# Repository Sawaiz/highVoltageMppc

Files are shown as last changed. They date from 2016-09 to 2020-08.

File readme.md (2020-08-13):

# MPPC High Voltage
Surface mount module that provides 52.5V to 57.5V in 20mV increments. Also contains a 2 input 24bit ADC to allow for closed loop control of the voltage, and read in a thermistor mounted near the sensor.

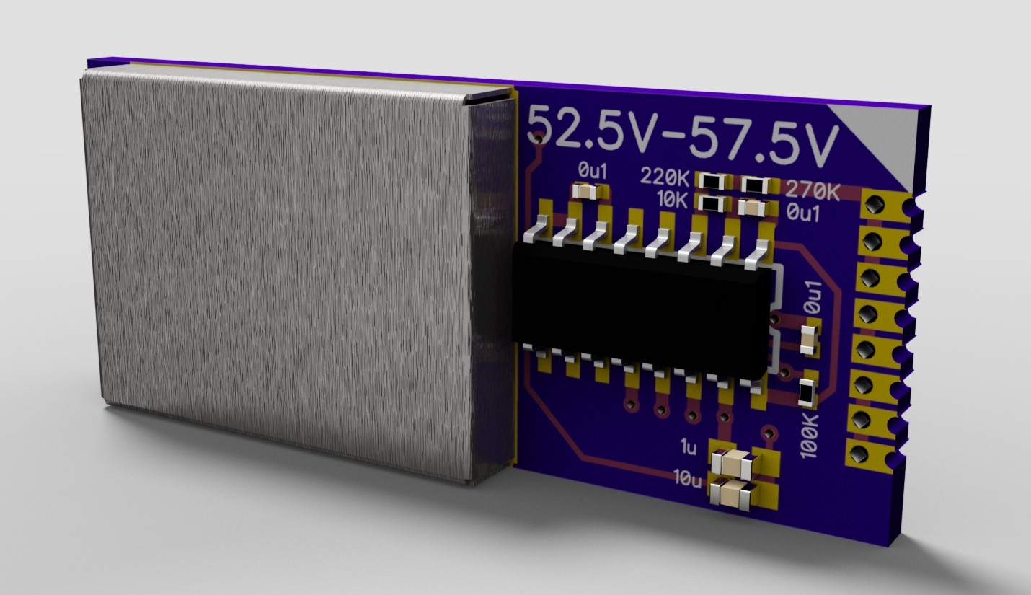
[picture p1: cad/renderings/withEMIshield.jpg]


## Hardware
The module uses a MAX1932 APD bias voltage boost converter and NAU7802SGI 24bit Analog to Digital converter (ADC) for reading temperature and output voltage.

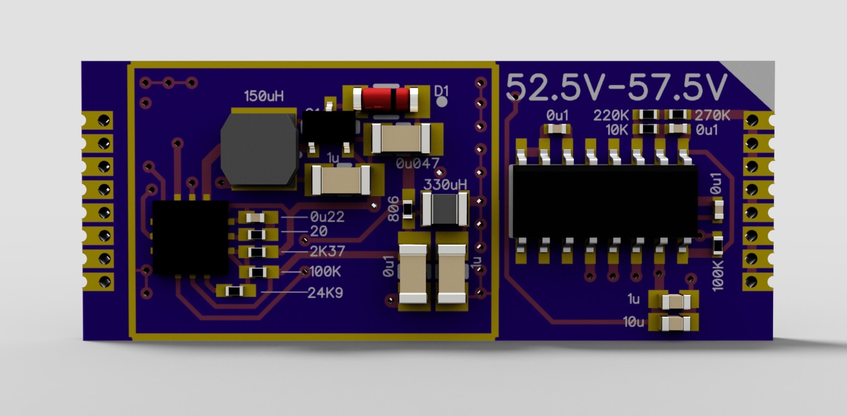
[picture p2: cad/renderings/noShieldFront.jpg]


### High Voltage
The module uses a [MAX1932](http://datasheets.maximintegrated.com/en/ds/MAX1932.pdf) APD bias voltage boost converter to maintain the output voltage. The voltage range, and step size is dictated with setting R2, R3, and R4. The minimum and maximum voltage set using the equations for on page 7 of the datasheet, and there are 8 bits (256) intermediate values that are possible. The high switching portion was designed with general SMPS design requirements (short high current loops, separated ground planes, EMI shielding) providing a low ripple output (<5mVpp ripple) and no significant back EMF.

### ADC
The analog to digital converter is a one designed for high precision and low sampling rate. The [NAU7802SGI](http://www.nuvoton.com/resource-files/NAU7802%20Data%20Sheet%20V1.7.pdf) is marketed at the load sensing market, but the high precision and low sampling rate lends itself well to the closed loop control and monitoring application. The high voltage is divided by 100 and the thermistor is put across a equivalent 100K static resistor to go along with he 100K NTC found on the MPPC sensor module to act as a voltage divider.

## Software
Each module has two buses that run to it. The following lists pins and their functions.

| Pin | Label | Description               |
| --- | ----- | ------------------------- |
|1    | 3V3   | Regulated 3.3V in         |
|2    | CS    | **SPI** bus Chip Select   |
|3    | SCLK  | **SPI** bus clock         |
|4    | DIN   | **SPI** bus data in       |
|5    | GND   | Common Ground             |
|6    | DRDY  | ADC conversion done       |
|7    | SCL   | **I2C** bus clock         |
|8    | SDA   | **I2C** bus data          |

### High Voltage
The SPI bus is connected directly to the MAX1932. Chip select is active low and data is sent MSB (most significant bit first). Sending bytes to it sets the voltage. Setting them to 0x00 turns off the DC-DC converter portion. As values increase to 0xFF (127), the output voltage falls, linearly.

```Arduino
//Example Arduino code that loops through all voltages.
//SCLK --> Pin 13 for Uno or Duemilanove
//DIN ---> Pin 11 for Uno or Duemilanove

#include <SPI.h>
#define CS 2 //Any pin

void setup(){
	Serial.begin(9600);
	pinMode(CS, OUTPUT);
	digitalWrite(CS, HIGH);
	SPI.begin();
	SPI.setBitOrder(MSBFIRST);
}

void loop(){
	for(int i = 0 ; i < 256 ; i++){
		digitalWrite(CS, LOW);
		SPI.transfer(i);
		digitalWrite(CS, HIGH);
		Serial.println(i);
	}
}
```

### ADC
The ADC communicates through the I2C bus, the device address is permanently programed to *0101010* (0x2A). It is fully compliant with the I2C protocol and the datasheet has the register map (page 28) and protocol description (page 14).

```Arduino
//Example Arduino code to read back the two inputs.
#include <Wire.h>
unsigned long adcVal;

void setup(){
	Serial.begin(9600);
	Wire.begin();
}

void loop(){
	// step 1: instruct sensor to read
	Wire.beginTransmission(42); // transmit to device #42 (0x2A)
	Wire.write(byte(0x00));      // control address byte (0x)
	Wire.write(byte(0x00));      // data byte (0x)
	Wire.endTransmission();      // stop transmitting

	// step 2: wait for readings to happen
	delay(1000);

	// step 3: request reading from sensor
	Wire.requestFrom(42, 3);    // request 2 bytes from slave device #42

	// step 4: receive reading from sensor
	if (3 <= Wire.available()) { // if two bytes were received
		adcVal = Wire.read();      // receive byte one (overwrites previous reading)
		adcVal = adcVal << 8;      // shift byte to make room for new byte
		adcVal = Wire.read();      // receive high two
		adcVal = adcVal << 8;      // shift both bytes
		adcVal |= Wire.read();     // receive low byte
		Serial.println(adcVal);    // print the reading
	}
}
```

## Archived
Archived, HV intergrated into MPPC interface from v1.1.

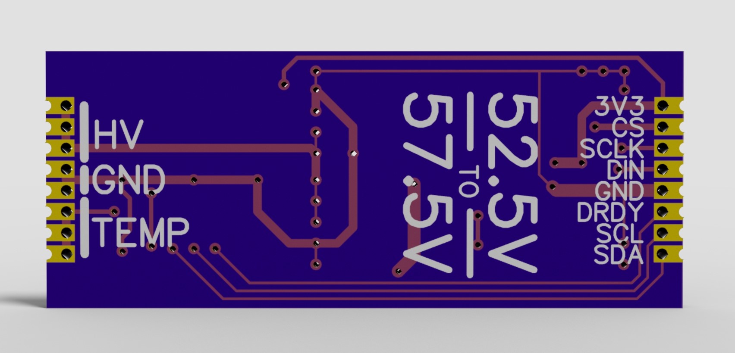
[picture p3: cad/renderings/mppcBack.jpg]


[mppcBack]: cad/renderings/mppcBack.jpg "View of Back of Board"
[noShieldFront]: cad/renderings/noShieldFront.jpg "Direct front view"
[withEMIshield]: cad/renderings/withEMIshield.jpg "Board rendering with EMI shield"

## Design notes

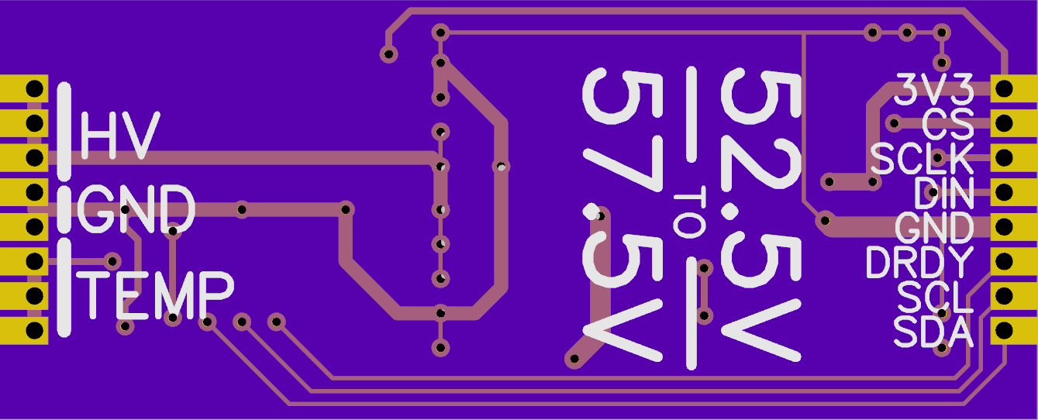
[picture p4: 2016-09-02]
cad/decal/highVoltageMppcBack.png

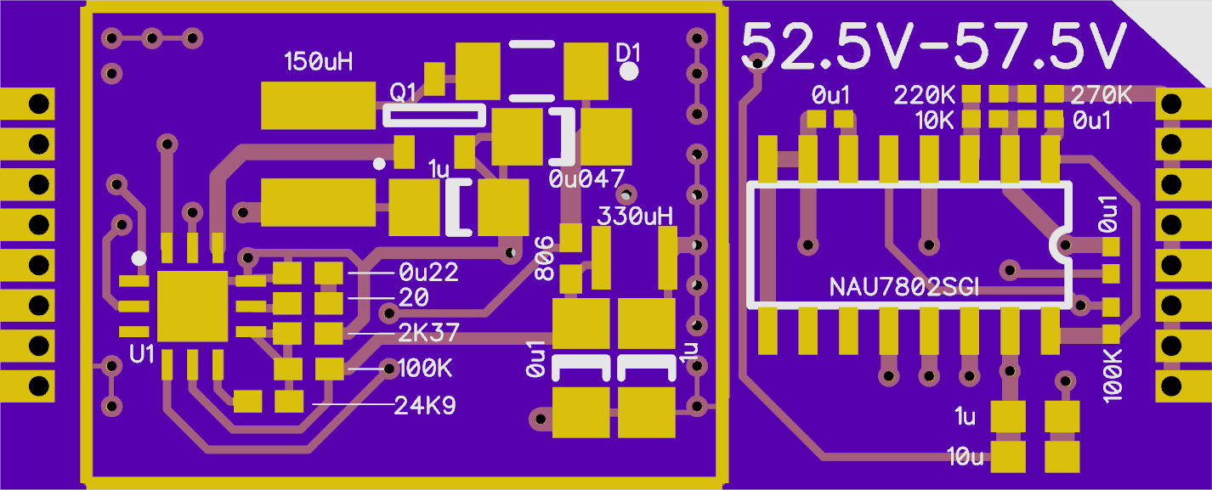
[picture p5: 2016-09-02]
cad/decal/highVoltageMppcFront.png

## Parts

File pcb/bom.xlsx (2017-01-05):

Ref-Des | Function | Description | P/N | Digikey P/N | QTY | Unit Price | Extended Price | URL
C1 | Input Decoupling | 1µF 16V Ceramic Capacitor X7R 1206 | 160R18W105KV4E | 709-1068-1-ND | 1 | $0.0890 | $0.09 | http://www.digikey.com/scripts/DkSearch/dksus.dll?Detail&itemSeq=188836551&uq=635911598142349451
C2 | Boost Capacitor | 0.047µF 500V Ceramic Capacitor X7R 1206 | C1206C473KCRACTU | 399-6743-1-ND | 1 | $0.1300 | $0.13 | http://www.digikey.com/scripts/DkSearch/dksus.dll?Detail&itemSeq=188836455&uq=635911598142339439
C3 | Pre Filter Capacitor | 0.10µF 250V Ceramic Capacitor X7R 1206 | C1206C104KARACTU | 399-4674-1-ND | 1 | $0.1485 | $0.15 | http://www.digikey.com/scripts/DkSearch/dksus.dll?Detail&itemSeq=188836482&uq=635911598142349451
C4 | Post Filter Capacitor | CAP CER 1UF 100V X7R 1206 | 12061C105KAT2A | 478-6226-1-ND | 1 | $0.1570 | $0.16 | http://www.digikey.com/scripts/DkSearch/dksus.dll?Detail&itemSeq=188836361&uq=635911598142339439
C5 | Compensation Capacitor | CAP CER 0.22UF 16V Y5V 0402 | CL05F224ZO5NNNC | 1276-1060-1-ND | 1 | $0.0112 | $0.01 | http://www.digikey.com/scripts/DkSearch/dksus.dll?Detail&itemSeq=188836589&uq=635911598142349451
D1 | Boost Diode | DIODE GEN PURP 100V 200MA SOD80 | LL4148 | LL4148FSCT-ND | 1 | $0.0420 | $0.04 | http://www.digikey.com/scripts/DkSearch/dksus.dll?Detail&itemSeq=188146539&uq=635911598142339439
L1 | Boost Inductor | FIXED IND 150UH 320MA 2.4 OHM | SRN4018-151M | SRN4018-151MCT-ND | 1 | $0.2400 | $0.24 | http://www.digikey.com/scripts/DkSearch/dksus.dll?Detail&itemSeq=188145546&uq=635911598142329427
L2 | Smoothing Inductor | FIXED IND 330UH 90MA 15.99 OHM | CBC2518T331K | 587-3059-1-ND | 1 | $0.1400 | $0.14 | http://www.digikey.com/scripts/DkSearch/dksus.dll?Detail&itemSeq=188145512&uq=635911598142319415
Q1 | Boost Switch | MOSFET N-CH 100V 0.17A SOT-23 | BSS123L | BSS123LCT-ND | 1 | $0.1032 | $0.10 | http://www.digikey.com/scripts/DkSearch/dksus.dll?Detail&itemSeq=188145567&uq=635911598142329427
R1 | Current Sens Resistor | RES SMD 806 OHM 0.1% 1/16W 0402 | RT0402BRD07806RL | YAG1481CT-ND | 1 | $0.1276 | $0.13 | http://www.digikey.com/scripts/DkSearch/dksus.dll?Detail&itemSeq=188837307&uq=635911598142359463
R2, R6 | Adjustment Span/Temp | RES SMD 100K OHM 0.1% 1/16W 0402 | RT0402BRD07100KL | YAG1343CT-ND | 2 | $0.1276 | $0.26 | http://www.digikey.com/scripts/DkSearch/dksus.dll?Detail&itemSeq=188837329&uq=635911598142359463
R3 | Minimum Voltage Res | RES SMD 2.37KOHM 0.1% 1/16W 0402 | CPF0402B2K37E1 | A102770CT-ND | 1 | $0.2082 | $0.21 | http://www.digikey.com/scripts/DkSearch/dksus.dll?Detail&itemSeq=188837419&uq=635911598142369475
R4 | DAC Resistor | RES SMD 24.9KOHM 0.1% 1/16W 0402 | RT0402BRD0724K9L | YAG1393CT-ND | 1 | $0.1276 | $0.13 | http://www.digikey.com/scripts/DkSearch/dksus.dll?Detail&itemSeq=188837348&uq=635911598142359463
R5 | Compensation Res | RES SMD 20 OHM 0.1% 1/16W 0402 | CPF0402B20RE1 | A102706CT-ND | 1 | $0.1973 | $0.20 | http://www.digikey.com/scripts/DkSearch/dksus.dll?Detail&itemSeq=188837408&uq=635911598142369475
U1 | Boost Controller | IC SUPPLY BIAS APD 12-TQFN | MAX1932ETC+T | MAX1932ETC+TCT-ND | 1 | $7.2828 | $7.28 | http://www.digikey.com/scripts/DkSearch/dksus.dll?Detail&itemSeq=188145609&uq=635911598142329427
U2 | ADC | IC ADC 24BIT I2C/SRL 16-SOP | NAU7802SGI | NAU7802SGI-ND | 1 | $1.3442 | $1.34 | http://www.digikey.com/product-search/en/rf-if-and-rfid/rf-shields/3539677?k=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
C6 | .1uF | 0.10µF 10V Ceramic Capacitor X5R 0402 | CL05A104KP5NNNC | 1276-1022-1-ND | 2 | $0.0048 | $0.01 | http://www.digikey.com/product-detail/en/murata-electronics-north-america/GRM155R71C104KA88J/490-6328-2-ND/2610892
C7 | 1uF | 1µF 6.3V Ceramic Capacitor X6S 0402 | GRM155C80J105KE15D | 490-6281-1-ND | 1 | $0.0055 | $0.01 | http://www.digikey.com/product-detail/en/murata-electronics-north-america/GRM155C80J105KE15D/490-6281-2-ND/2610795
C8 | 10uF | 10µF 6.3V Ceramic Capacitor X5R 0603 | GRM155R60G106ME44D | 490-10693-1-ND | 1 | $0.0380 | $0.04 | http://www.digikey.com/product-detail/en/murata-electronics-north-america/GRM155R60G106ME44D/490-10693-2-ND/4905101
S1 | RF Shield | RFI SHIELD CAN 20X15X3MM | S02-20150300 | 952-2632-ND | 1 | $3.5300 | $3.53 | http://www.digikey.com/product-search/en/rf-if-and-rfid/rf-shields/3539677?k=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
R7 | 220k 1% | RES SMD 220K OHM 1% 1/16W 0402 | RC0402FR-07220KL | 311-220KLRCT-ND | 1 | $0.0054 | $0.01 | http://www.digikey.com/scripts/DkSearch/dksus.dll?Detail&itemSeq=203632236&uq=636058256422392383
R9 | 270k 1% | RES SMD 270K OHM 1% 1/16W 0402 | RC0402FR-07270KL | 311-270KLRCT-ND | 1 | $0.0054 | $0.01 | http://www.digikey.com/scripts/DkSearch/dksus.dll?Detail&itemSeq=203632249&uq=636058256422402384
R8 | 10k 0.1% | RES SMD 10K OHM 1% 1/16W 0402 | RC0402FR-0710KL | 311-10.0KLRCT-ND | 1 | $0.0054 | $0.01 | http://www.digikey.com/scripts/DkSearch/dksus.dll?Detail&itemSeq=203632266&uq=636058256422402384

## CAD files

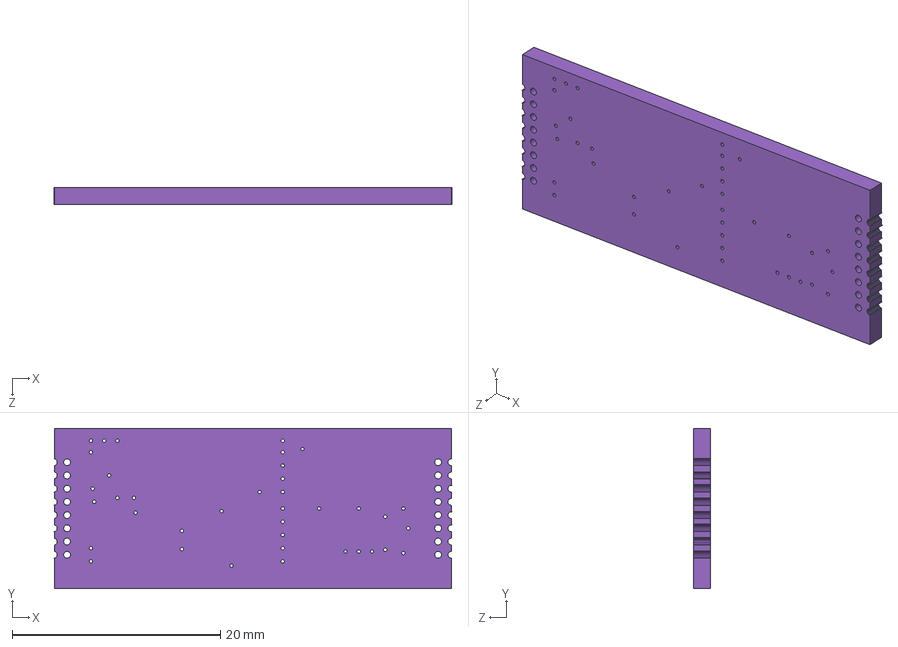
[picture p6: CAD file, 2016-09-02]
cad/highVoltageMppc.step
38.2 x 15.4 x 1.60 mm

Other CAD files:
cad/electronics/2.54 Breakaway/1x1.iam
cad/electronics/2.54 Breakaway/1x6.iam
cad/electronics/2.54 Breakaway/Holder.ipt
cad/electronics/2.54 Breakaway/Pin.ipt
cad/electronics/2.54 Breakaway/PinRight1.ipt
cad/electronics/2.54 Breakaway/PinRight2.ipt
cad/electronics/S02-20150300.ipt
cad/electronics/SOP-16.ipt
cad/electronics/SOT23-3.ipt
cad/electronics/SRN4018.ipt
cad/electronics/capacitor-0402.ipt
cad/electronics/capacitor-0603.ipt
cad/electronics/capacitor-1206.ipt
cad/electronics/capacitor.ipt
cad/electronics/chipResistor.ipt
cad/electronics/chipResistor/chipResistor-0402.ipt
cad/electronics/inductor-1007.ipt
cad/electronics/inductor.ipt
cad/electronics/qfn.ipt
cad/electronics/qfn/qfn-12.ipt
cad/electronics/sod-80.ipt
cad/highVoltageMppcBoard.iam
cad/highVoltageMppcBoard.ipt

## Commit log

2016-03-02 Cad Design Done
    [1x6.iam, 2x4RibbonConnector.ipt, 2x4header.ipt, 788640001.iam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]
2016-03-27 Batch of 24 made
    [1x1.iam, 1x6.iam, highVoltageMppc.iam, pcb.ipt]
2016-04-06 Remaned PCB file to avoid confilts when used as dependecy
    [highVoltageMppcPcb.ipt]
2016-04-06 Reloaded project to fix pcb path
    [1x1.iam, 1x6.iam, highVoltageMppc.iam]
2016-04-06 Renamed Decal FIles to prevent clashes
    [highVoltageMppcPcb.ipt]
2016-06-28 added sop16
    [Board.ipt, SOP-16.ipt, capacitor-0603.ipt, highVoltageMppc.iam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]
2016-06-28 Updated Decals and step
    [highVoltageMppc.step]
2016-06-28 Corrected pacakge of ADC
    [Board.ipt, SOP-16.ipt, capacitor-0603.ipt, highVoltageMppc.iam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]
2016-06-28 edited emi shield
    [S02-20150300.ipt, S02-30200250.ipt]
2016-06-29 cropped decals
    [Board.ipt, highVoltageMppcBoard.ipt]
2016-06-29 updated step file
    [highVoltageMppc.step]
2016-06-29 rendered pictures and finalized assembly
    [S02-20150300.ipt, highVoltageMppcBoard.iam, highVoltageMppcBoard.ipt]
2016-06-30 assembled mppcHighVoltage board
    [capacitor-0402.ipt, capacitor-0603.ipt, capacitor-1206.ipt, chipResistor-0402.ipt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]
2016-06-30 updated board
    [highVoltageMppcBoard.iam]
2016-07-08 Added Readme, wiht code samples and all
2016-07-08 updated renderings
    [S02-20150300.ipt, capacitor-0402.ipt, capacitor-0603.ipt, capacitor-1206.ipt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]
2016-07-08 Updated Bom
    [bom.xlsx]
2016-08-03 updated assemblies
    [S02-20150300.ipt, highVoltageMppcBoard.iam, highVoltageMppcBoard.ipt]
2016-08-03 Changed div resistors, added caps.
2016-08-03 Updated some ref des
    [bom.xlsx]
2016-08-04 updated board, created new .step files and decals
    [highVoltageMppc.step, highVoltageMppcBoard.iam, highVoltageMppcBoard.ipt]
2016-08-04 updated board and renderings
2016-09-02 Changed 3V3 to VDD to reflect larger voltage range
2017-01-05 Still 2016 version will likey change soon
    [bom.xlsx, highVoltageMppcBoard.iam, highVoltageMppcBoard.ipt]
2017-01-07 Upgraded to Inventor 2017 files
    [S02-20150300.ipt, SOP-16.ipt, SOT23-3.ipt, SRN4018.ipt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]
